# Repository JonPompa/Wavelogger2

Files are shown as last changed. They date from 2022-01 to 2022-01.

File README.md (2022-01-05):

# Wavelogger2
Underwater Pressure and Temperature logger

This project is for making a pressure / temperature logger from commercially available parts. 
The loggers run approximately 2 weeks on a battery charge and can log at a frequency of ~20Hz down to once per 30 seconds. 
THe depth limit under water is ~300m, as set by the pressure sensor. 
Data is stored on a micro SD card.

The project is inspired by Luke Miller's Open Wave Height Logger project and copies heavily from his work.
Most electrical hardware is sourced from Adafruit and the base of code is derived from their example code for the adalogger hardware.
All pressure tolerant hardware is sourced from Blue Robotics. They also provide the library for interpreting the pressure and temperature sensors.

Included files here are:
1) operating instructions for the loggers (This includes a bill of materials if anyone wants to source and build their own)
2) clock setting software for the persistent clock - direct from Adafruit
3) Operating software for the logger in its logging state
4) CAD fies for the parts tray used inside the blue robotics pressure housing
5) An assembly diagram and instructions will be developed if anyone asks for them! ( This can include a more detailed bill of materials with purchasing links)

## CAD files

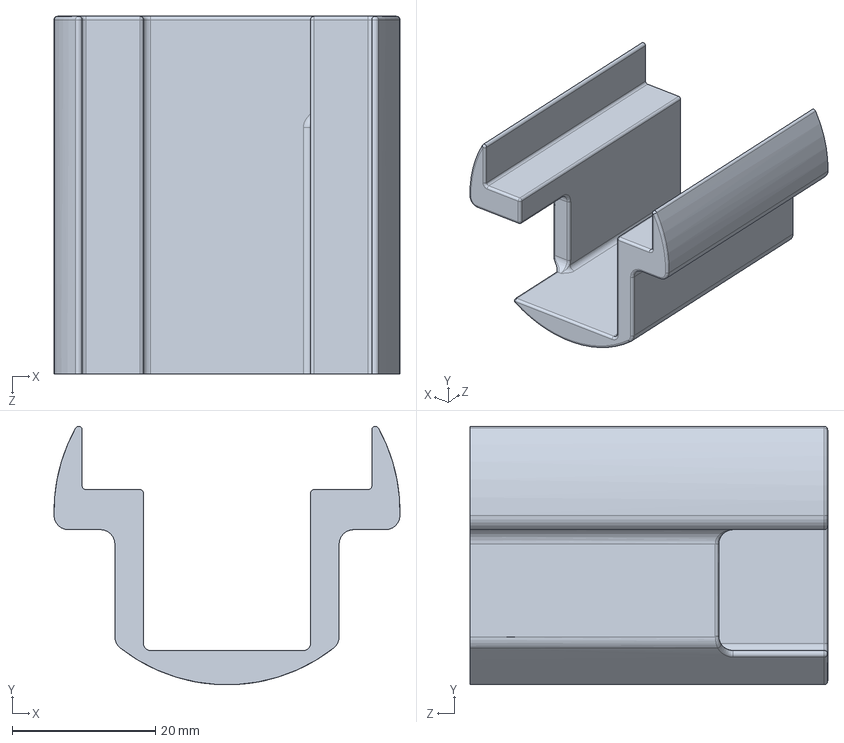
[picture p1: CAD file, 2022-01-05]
parts holder R3.SLDPRT
48.4 x 36.1 x 50.0 mm

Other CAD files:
parts holder R3.STL

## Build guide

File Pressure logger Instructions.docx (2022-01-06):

# Pressure Logger Instructions

# Overview

This pressure logger is intended for high rate, short duration pressure logging in water (ocean and fresh). Examples of typical use include wave height monitoring, coordinated tide and temperature observations, and storm surge observation.

# Specifications

Value | Range | Resolution
Depth Rating | 300m (limited by sensor)
Data Parameters
Temperature | 2-40 degrees C | 0.01 Deg C (accuracy +/- 1.5C)
Pressure | 0-30 Bar absolute | 0.2 mBar (accuracy +/- 200 mBar)
Battery Voltage | 0-5 Volts | 0.01V
Sampling Frequency | 0.5 to 20 Hz | 1 ms timing interval
Battery Capacity | 4500 mAh @ 3.7V (~14 days run time)

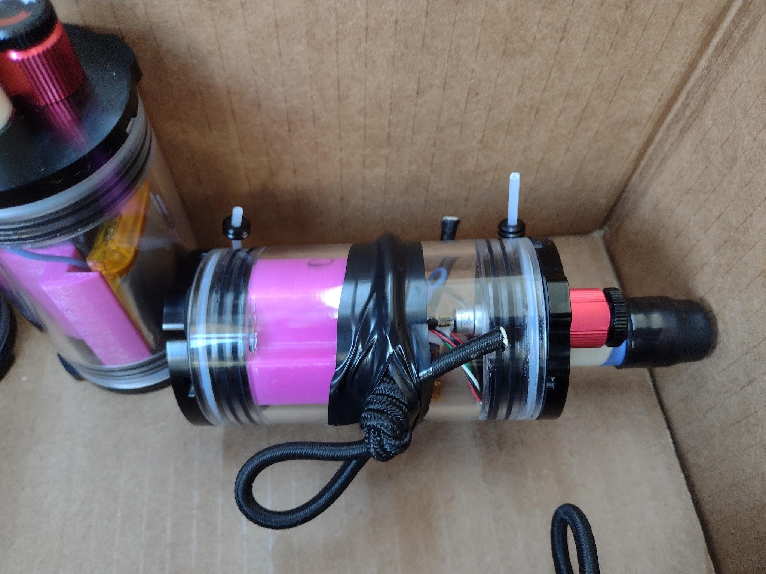
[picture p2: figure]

Pressure Logger fully assembled

# Electronics

The logger is made using an adafruit 32u4 data logger board (https://learn.adafruit.com/adafruit-feather-32u4-adalogger) and an adafruit RTC clock unit (https://learn.adafruit.com/ds3231-precision-rtc-featherwing)

The pressure sensor is from Blue Robotics (https://bluerobotics.com/store/sensors-sonars-cameras/sensors/bar30-sensor-r1 ). It includes an MS5837 absolute pressure sensor housed in a pass-through that fits into the pressure housing endcap. This sensor is rated to 300m and has a pressure resolution of 0.2 millibar. (equivalent to 2mm water depth).

Tests have shown the system maintains a noise level below 0.5 mBar in a static environment. Drift over long periods (hours) has not been well characterized yet as it needs to be compared against well-calibrated barometric pressure sensors.

The pressure sensor is not rated for continuous contact with water (readings drift), so it is protected from water by operating in a mineral-oil filled chamber. The oil is kept in the chamber by a membrane (made of a nitrile glove finger) which transmits pressure from the external water to the interior oil without influencing the pressure. This nitrile membrane is protected from damage by a rubber cap with a small hole to allow water flow.

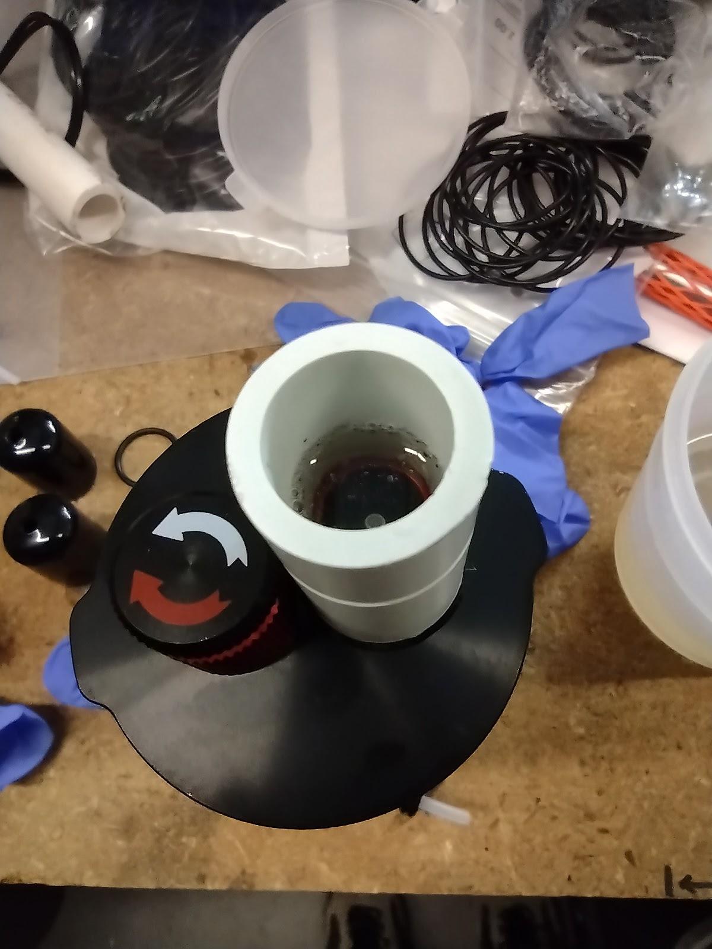
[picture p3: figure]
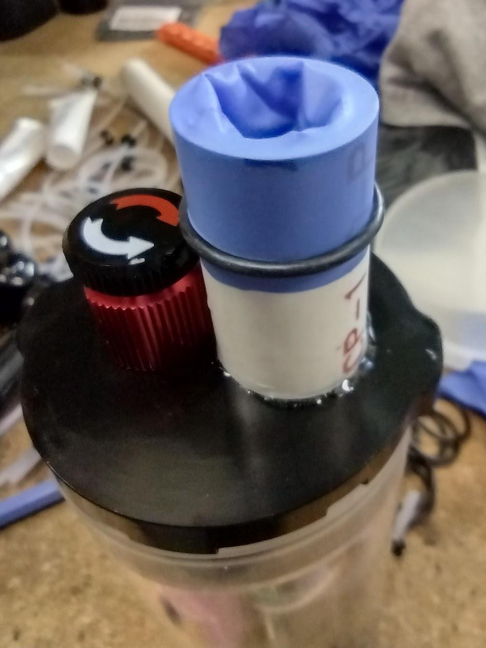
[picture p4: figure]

The pressure sensor is covered in a protective tube filled with mineral oil and covered with a nitrile membrane.

# Battery

The logger is provided with a 4500mAh battery. It is a single cell battery providing an average 3.7V with a working range from 3.2V to 4.2V. The adafruit logger board automatically turns off when the voltage reaches a minimum to avoid damaging the battery.

*NOTE ON POLARITY: The batteries provided with the loggers are wired in a “normal” direction with pin 1 of the connector negative and pin 2 positive. The Adafruit logger has a connector polarity reversed from almost all other devices that use the same connectors and battery types so it is provided with a short extension cable to reverse the polarity. When plugging in a battery, always make sure this cable is in place in the logger. When charging, always plug the battery directly into a charger without the extension cable.

There is a lithium button cell battery in the Clock board which provides constant backup power to retain the clock’s date and time reference when the main battery is removed. This is a lithium CR2012 size button cell.

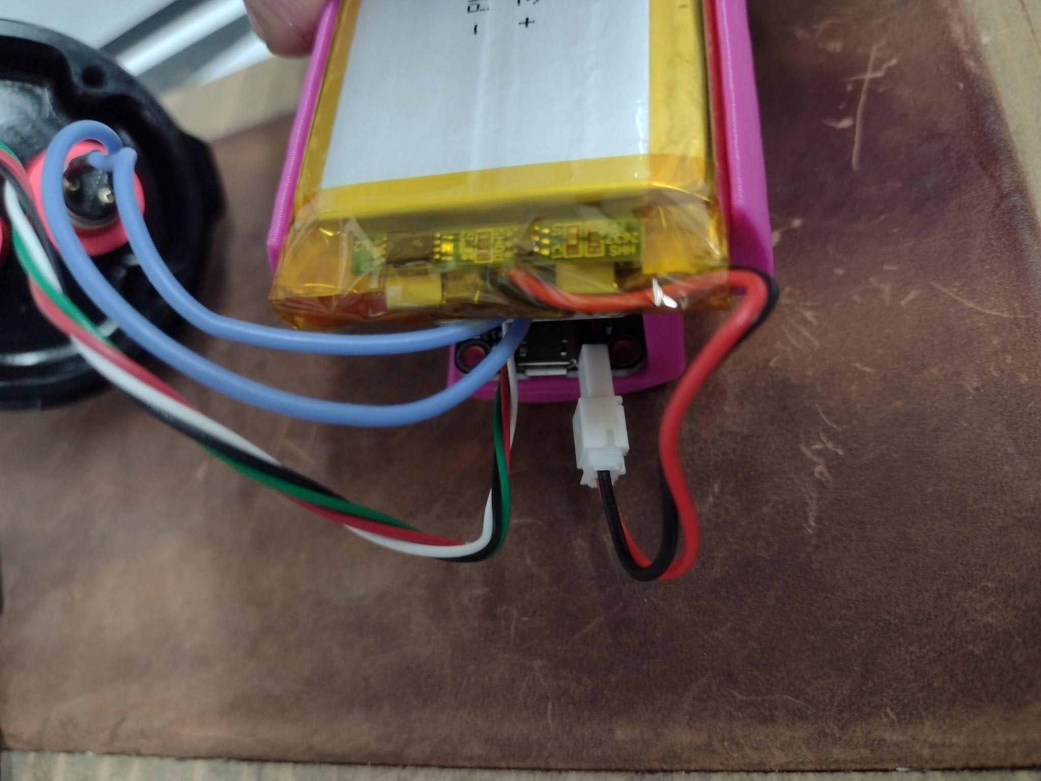
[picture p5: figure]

Battery connector: Always disconnect the battery here, not at the side of the board. The battery connector polarity is correct for the charger directly from the battery. The extension cable hidden between the circuit boards reverses the polarity for the adafruit board and should never be plugged into a charger.

# Charging

When the logger is plugged into a USB port, an internal battery charging circuit will charge the LiPo battery at a rate of 0.1A. A yellow light next to the USB port on the logger board will indicate charging is active. The light will turn off when the battery is fully charged at 4.2V. This charge rate is very low for the capacity of battery provided (4500mAh) and charging this way will take approximately 45 hours.

Using an external charger is recommended. A charger should be provided with the loggers which is capable of charging 6 batteries simultaneously at 0.6A rate.

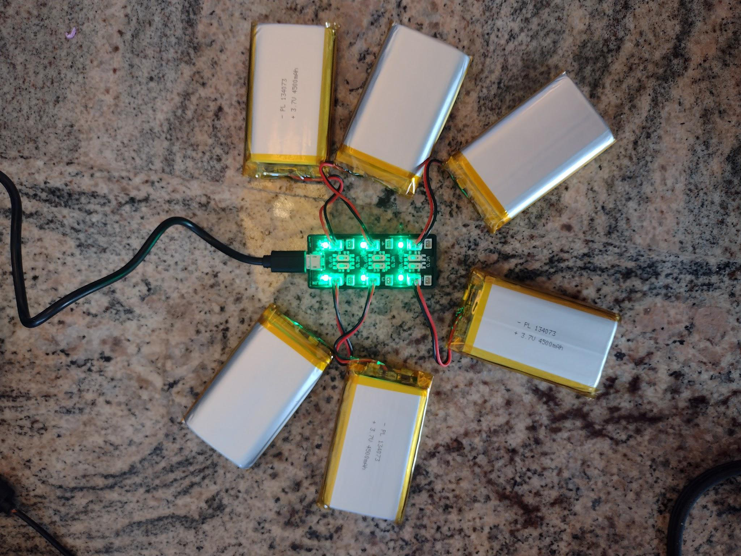
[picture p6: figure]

6 batteries attached to the external charger

# Software

Assembled loggers are pre-programmed when shipped and do not need to be programmed to record data. As of this writing, they are shipped with 4Hz sampling rate. If you prefer to change the logging parameters (such as sampling interval) you should follow the instructions below to reprogram them.

It may be helpful to reprogram the loggers occasionally to update the clock time if it has drifted or if the clock battery needs to be replaced.

The logger is programmed in the Arduino environment: Arduino IDE (download at https://www.arduino.cc/en/software)

Instructions for connecting a logger and installing are here (https://learn.adafruit.com/adafruit-feather-32u4-adalogger/setup). This gives instructions for adding the required libraries to the Arduino environment to compile this code.

The loggers should be distributed with the Arduino code sketches needed to run them,

Wavelogger2.ino and ds3231.ino, both available at https://github.com/JonPompa/Wavelogger2

The logger board has a USB port on it and can be connected with a USB cable to a computer running the Arduino IDE for programming.

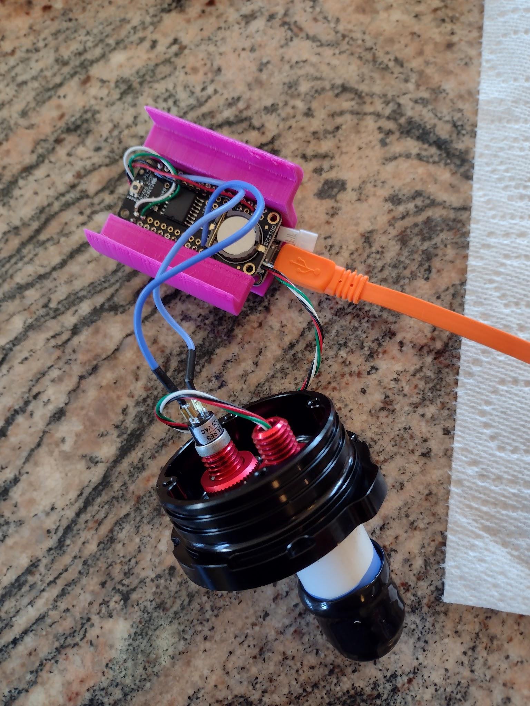
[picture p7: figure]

The logger can be connected to a computer to program it using a USB cable attached to the USB port on the logger board. This port also charges the battery (slowly) from the USB port.

Arduino sketch Ds3231.ino is used to set the RTC clock on the logger and should only need to be used once when the logger is first powered or when the button cell backup battery is replaced. DS3231.ino should be uploaded to the logger through the Arduino IDE. You can verify success by opening a serial terminal and seeing confirmation of the current time and date. (ctrl+shift+m opens a terminal window in a windows environment) The baud rate of the terminal window should be set to 56700 or whatever rate is specified in the version of ds3231.ino that you are using)

Wavelogger2 is the main program running the data collection. It should be compiled and uploaded to the logger after the ds3231.ino clock setting sketch is run. In this program, there is a set of user parameters to set for the interval between data pushes to the log file and also for frequency of sampling. The sampling interval is given in milliseconds. Know that there is also a 50ms sampling duration added to the period you specify, for example, an interval of 200ms will mean a total time between samples of 250ms, leading to a 4Hz actual sample rate.

Code example:

//User settings//

int logInterval = 4000; //milliseconds between data saves to the SD card *note max of 32000 allowed with an int data type

int senseInterval = 200; //milliseconds between data read attempts for pressure and temp sensor.

//Data reading +overhead takes about 50ms so a value of 200 here gives ~4Hz,

//Fastest achievable is about 18Hz by setting senseInterval low (5ms)

bool recordBatVolts = true; //record or don't record battery voltage

Log files are started when power is turned on. The log files are named for the date on which they start, using year, month, day format. i.e. 20210131.txt

# Assembly

The logger housing must be opened to access the data port and card reader. Once the logger has been appropriately programmed, it is not necessary to plug it into a computer to restart logging. Inserting a data card and turning on power will always initiate logging.

It is recommended to open the logger from the sensor endcap end.

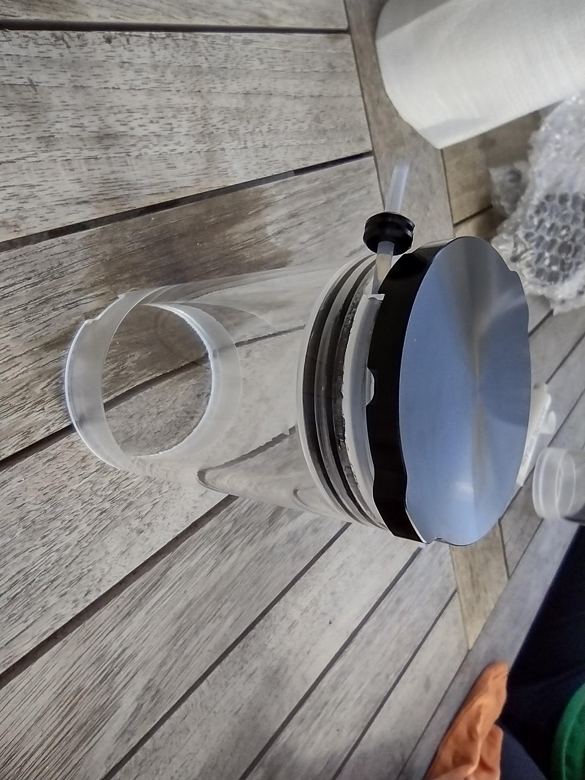
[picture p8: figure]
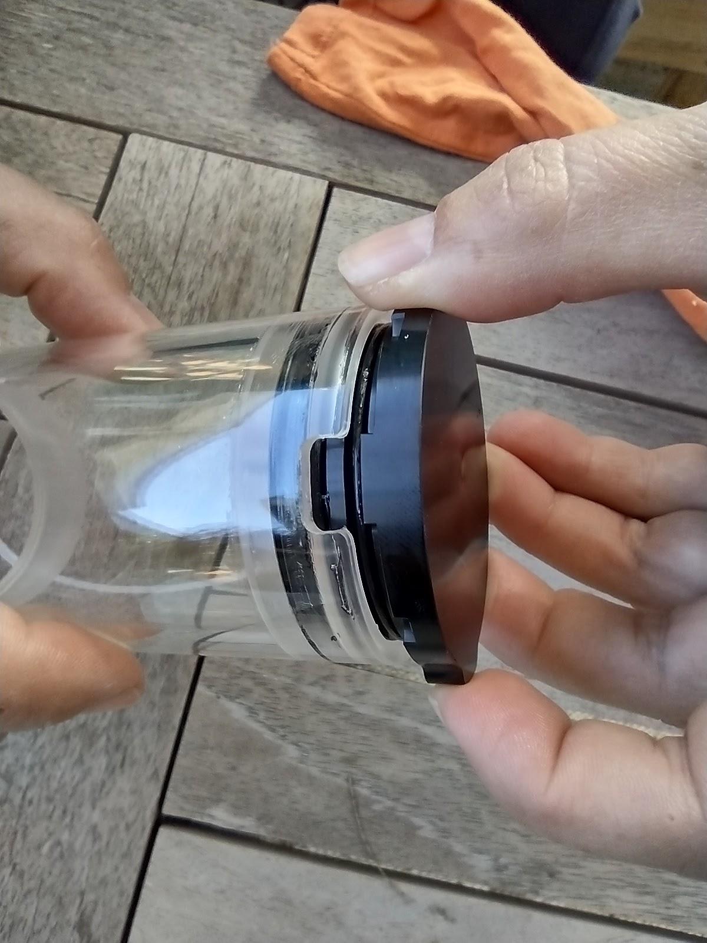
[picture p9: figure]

Opening an endcap is achieved by pulling the white plastic cord then gently sliding the endcap out by hand. Before closing an endcap, always clean and inspect orings. The orings should be lubricated with silicone grease.

To assemble the logger, slide the electronics tray (with battery) into the housing, being careful to seat the battery into the blank endcap and to align the switch and battery so that they don’t interfere. The end cap with the sensors must be rotated so that its tab aligns with the notch in the housing body for it to seat fully. See images below for important alignment notes.

The following images show some important details of how the parts fit together.

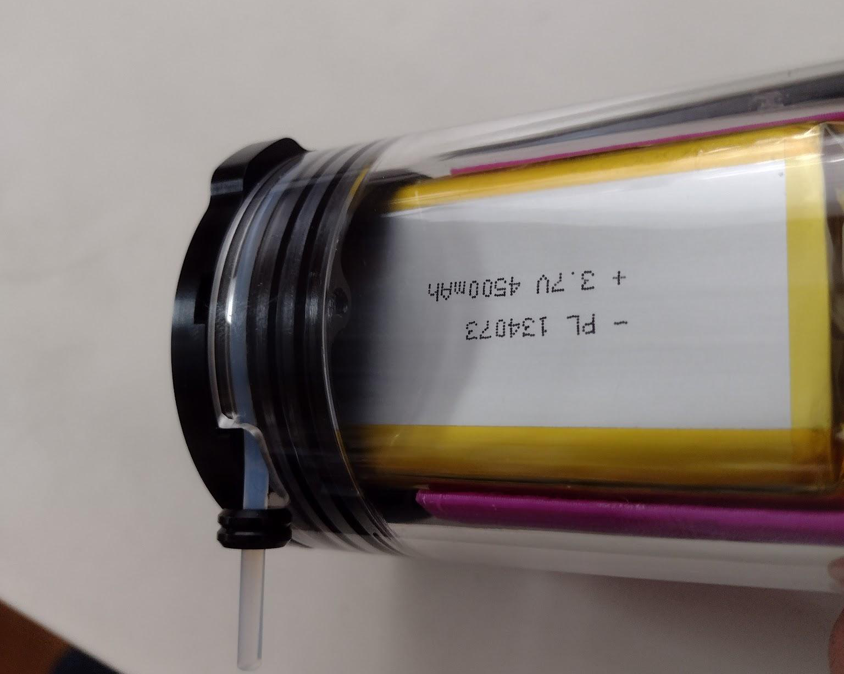
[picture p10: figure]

The battery fits down into the blank endcap when the battery and electronics tray are inserted fully into the pressure housing as shown here. This is only possible at some angles because of the shape of the endcap interior.

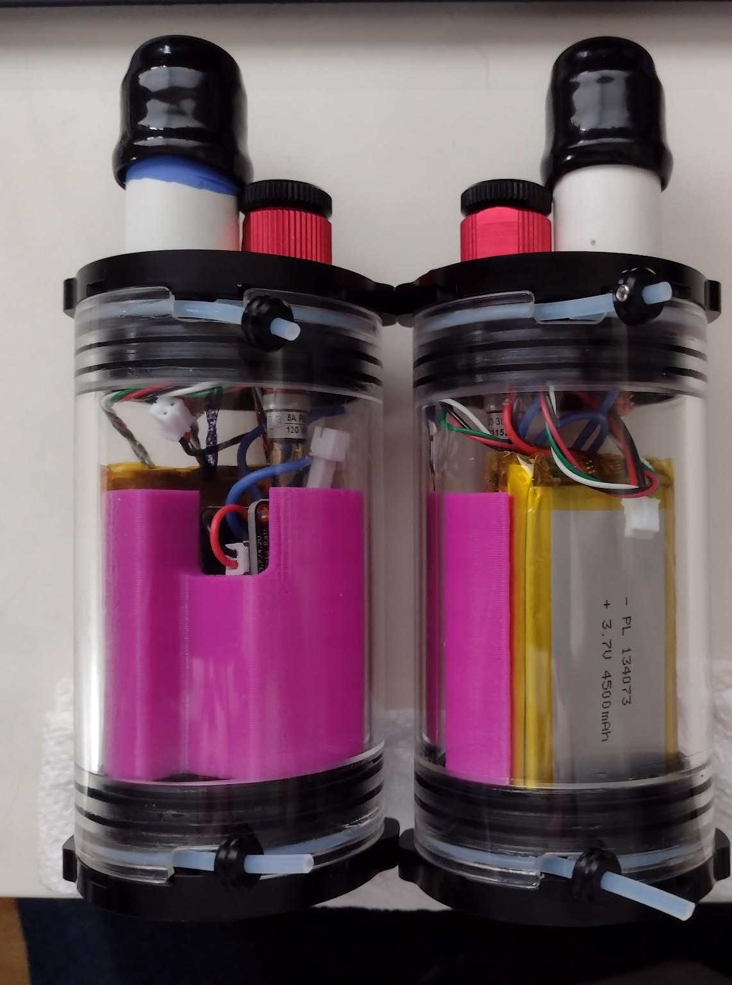
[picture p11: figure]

This image shows mirrored versions of the logger endcap. Unfortunately, some loggers were built in each configuration and the configurations require attention to assemble correctly. The notch in the housing that allows insertion of the locking cord must align with a small tab on the endcap. That alignment sets the position of the switch in the endcap. Because the switch terminals extend downward far enough to interfere with the battery, the electronics tray must be rotated to place the battery under the sensor side of the endcap, not the switch. Please pay attention to this when assembling the loggers!

The housing is sealed with o-rings on the circumference of the end caps. When the housing is assembled, the rubber o-rings must be inspected, cleaned (very carefully look for threads, fibers, and hair on the rings), and lightly greased with silicone grease.

When the end caps are pushed in, it may be helpful to remove the top of the power switch completely. This allows air to vent from the housing through a small hole (this also turns the logger on). Once the end caps are seated, they should be fastened by sliding the plastic lock cords around the circumference of the housing in the locking groove. The power switch top may then be re-inserted, being careful to note whether it is set in the on or off state. It is also helpful to inspect and grease the o-rings of the switch at this time.

# Power Switch

The logger housing can be assembled with the switch in the off position. This is when the switch top is fully screwed into the base.

At deployment time, the logger can be turned on by twisting the switch approximately one half turn in the unscrewing direction (counterclockwise).

Verify that the logger is recording by watching for an intermittent flashing of a red LED on the processor board next to the USB port. The red light flashes when data is written to the SD card, so if you have a short data writing interval, it flashes often and if you have a long data writing interval, it flashes seldom.

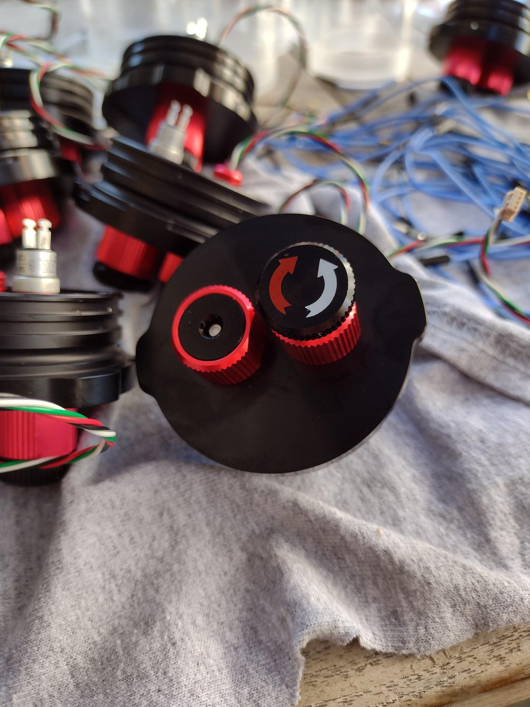
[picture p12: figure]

Here the power switch is shown on the end cap next to the bare pressure sensor. On finished loggers, the pressure sensor is protected by a cover.

# Data

Whenever the logger is turned on, it immediately starts recording data. Data is appended to an existing file if the logger has been started more than once in a day. It will start a new file if it is turned on during a new day.

Data is stored on a micro SD card which is inserted into the logger board (at the end opposite from the sensors and USB port). This card should be formatted in FAT32 format to work with the software.

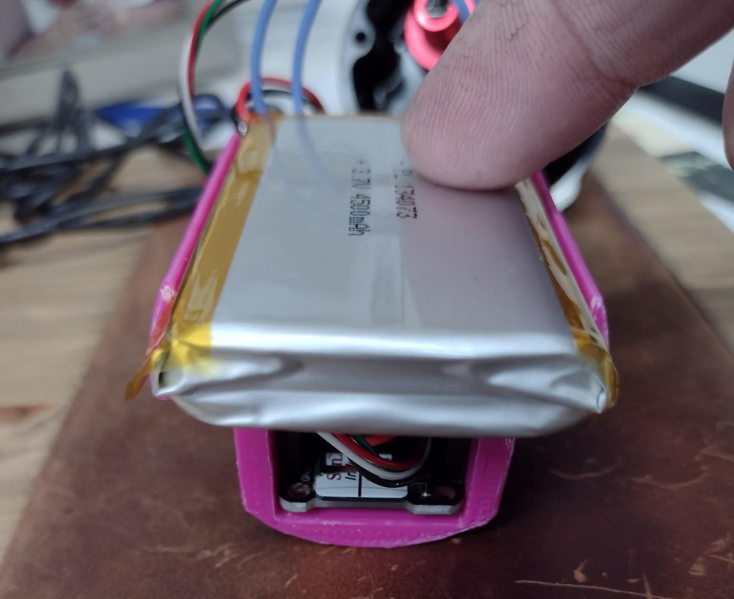
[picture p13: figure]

The SD card can be seen in its slot under the battery in this image of the disassembled logger.

Data is recorded in ASCII text format. The data fields include a header line explaining the columns. The data includes time in year, month, day, hour, min, sec, and milliseconds. The millisecond value is not referenced to the seconds value, and so may roll over independently from the count of seconds.

The data columns are:

Year Month Day Hour Minute Second Milliseconds Pressure Temperature BatteryVolts

Data for temperature is recorded in degrees C.

Data for pressure is provided in absolute millibars.

Battery voltage is recorded in volts.

*Note that as battery voltage drops for the last few hours of recording, before the low voltage cutoff shuts off the logger, the pressure reading will drift upward by several millibar.

At the time of this writing, there is no provision for retrieving data from the logger other than manually extracting the microSD card and reading it in another device. Future improvements include implementing a set of commands to retrieve the data via the USB connection and to add a USB connection through a connector on the pressure housing to prevent the need to open the loggers after each deployment.

# Data Processing

This logger records data files that become large quickly – i.e. hundreds of megabytes over a few days. Typically processing the data is best done in a scientific programming language set up for such data. Examples would be the R language, Matlab, or Python with NumPy.

A few notes on importing data follow

1) The files have a header row. This header row gives column names. If the logging was restarted within a 24 our period, there will be an extra copy of this header line in the data for each restart instance. This may challenge your data importing script!
2) The pressure data is in absolute pressure. The sensor is sensitive enough to track barometric pressure very well, so your pressure data processing may need to include an effort to obtain a local barometric pressure record and subtract that pressure from the recorded data. You may be able to use an on-shore logger to serve as a reference pressure recorder if you have a spare logger available.
3) Battery voltage is included as a debugging and convenience feature. You can reduce the data file size by turning off battery voltage logging (set the battery logging parameter value to “false” in the wavelogger2.ino file).
4) Battery voltage will influence the pressure reading when the battery is very low. Do not use the last few hours of the pressure record before the logger shuts down due to low battery state. The pressure reading will drift upward during that time.

# Mounting

The logger can be attached to a mounting location with cable ties, hose clamps, or other purpose-made clamps around the housing body. If using hose clamps, you may want to cover the clamp in a rubber tube such as a bicycle tire inner tube to prevent scratching the housing. If using cable-ties, it is suggested to avoid nylon cable ties which lose a significant amount of their strength when submerged in water over time.

# Credits

This manual is a living document and is subject to change.

This logger has been designed by Jon Pompa using readily available parts and code as referenced above.

Major inspiration was taken from Luke Miller’s Open Wave Height Logger project (which provides a much higher level of documentation, testing, and a longer-duration logger design)

Much of this project is also built on the Adalogger family of devices from Adafruit which provide nearly complete hardware and software out of the box.

The underwater housings and sensors are stock items from Blue Robotics.

# Contact

Please direct questions or ideas to Jon Pompa - jon@reefgen.io

Plans for incremental upgrades at the moment include data access and battery charging by connector, better wire management, and mounting brackets.

If anyone wants a construction manual for building these loggers, please make a request.

# Bill of Materials

Part | | Qty
Pressure housing
| Blue robotics 2" x 100mm housing | 1
| Blue robotics 2" blank endcap with flange | 1
| Blue robotics 2" endcap 2 hole with flange | 1
| BR switch / vent penetrator (modified to vent) | 1
| BR Bar30 pressure sensor | 1
| BR sealing cord (included with endcaps) | 2
| BR sealing orings (included with endcaps) | 4
Electronics
| Adafruit Adalogger 32u4 | 1
| Adafruit precision RTC featherwing | 1
| SD card | 1
| stacking header pins | 2
| header pins (included with adalogger) | 1
| Lipo single cell 4500mAh 13x40x72mm | 1
| CR1220 button cell (3V lithium) | 1
| Mounting bracket (parts holder_R2.sldprt) | 1
Sensor protection
| PVC 1/2 pipe bored out for sensor plus oring groove | 1
| 5min epoxy (gorilla) to seal pvc to sensor | 1
| Nitrile glove finger | 1
| mineral oil | 1
| Rubber cap (with hole) to go over pvc pipe | 1
| oring m2x17.5 | 1

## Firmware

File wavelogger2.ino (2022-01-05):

//Pressure and temperature logger to run on an adafruit adalogger 32u4 with precision RTC featherwing board
//Set your sampling frequency using "senseInterval" variable. Log writing frequency is independent of sampling frequency and can be set by logInterval
//battery voltage logging can be turned on or off
//To set the rtc, use sketch "ds3231" in the RTC examples

#include <MS5837.h>
#include <Wire.h>
#include <RTClib.h>
#include <SD.h>
#define VBATPIN A9 
MS5837 sensor;
RTC_DS3231 rtc;

//User settings//
int logInterval = 4000; //milliseconds between data saves to the SD card *note max of 32000 allowed with an int data type
int senseInterval = 200; //milliseconds between data read attempts for pressure and temp sensor. 
                        //Data reading +overhead takes about 50ms so a value of 200 here gives ~4Hz,
                        //Fastest achievable is about 18Hz by setting senseInterval low (5ms)
bool recordBatVolts = true; //record or don't record battery voltage


unsigned long lastSenseMils = 0;
unsigned long lastLogMils = 0;
File logFile;
int led = 13;

void setup() {
  Serial.begin(57600);
  //add a light so we can see the file write is happening

  pinMode(led, OUTPUT); 
  Serial.println("Starting");
  if (! rtc.begin()) {
    Serial.println("Couldn't find RTC");
    abort();
  } 

  delay(2000);
  openLogFile();
  
  Wire.begin();
  // Initialize pressure sensor
  // Returns true if initialization was successful
  // We can't continue with the rest of the program unless we can initialize the sensor
  while (!sensor.init()) {
    Serial.println("Pressure sensor init failed!");
    delay(1000);
  }
  // .init sets the sensor model for us but we can override it if required.
  // Uncomment the next line to force the sensor model to the MS5837_30BA.
  sensor.setModel(MS5837::MS5837_30BA);
  sensor.setFluidDensity(1029); // kg/m^3 (freshwater, 1029 for seawater)

}

void loop() {
  // put your main code here, to run repeatedly:
  if( (millis()-lastSenseMils) > senseInterval){
    doSensing();
    lastSenseMils = millis();
  }
  if( (millis()-lastLogMils) > logInterval){
    digitalWrite(led, HIGH);   // turn the LED on (HIGH is the voltage level)
    logFile.flush();
    lastLogMils = millis();
    digitalWrite(led, LOW);   // turn the LED on (HIGH is the voltage level)
  }
  //delay(10);
}

void doSensing() {
  // Update pressure and temperature readings
  sensor.read();
  
  /* //Serial debug
  Serial.print("Pressure: ");
  Serial.print(sensor.pressure());
  Serial.println(" mbar");

  Serial.print("Temperature: ");
  Serial.print(sensor.temperature());
  Serial.println(" deg C");

  Serial.print("Depth: ");
  Serial.print(sensor.depth(),4);
  Serial.println(" m");

  Serial.println(millis()%1000);
  */
  
  DateTime now = rtc.now(); 
  logFile.print(now.year(), DEC);logFile.print(' ');
  logFile.print(now.month(), DEC);logFile.print(' ');
  logFile.print(now.day(), DEC);logFile.print(' ');
  logFile.print(now.hour(), DEC);logFile.print(' ');
  logFile.print(now.minute(), DEC);logFile.print(' ');
  logFile.print(now.second(), DEC);logFile.print(' ');
  logFile.print(millis()%1000);logFile.print(" ");
  
  logFile.print(sensor.pressure());logFile.print(" ");
  logFile.print(sensor.temperature());logFile.print(" ");

  if(recordBatVolts){
    float measuredvbat = analogRead(VBATPIN);
    measuredvbat *= 2;    // we divided by 2, so multiply back
    measuredvbat *= 3.3;  // Multiply by 3.3V, our reference voltage
    measuredvbat /= 1024; // convert to voltage
    logFile.println(measuredvbat);
    //Serial.print("VBat: " ); Serial.println(measuredvbat);
  } else{           
     logFile.println(" ");
  }
}


void openLogFile(){
  Serial.print("Initializing SD card...");
  pinMode(4, OUTPUT);
 
  if (!SD.begin(4)) {
    Serial.println("initialization failed!");
    return;
  }
  Serial.println("SD initialization done.");
  
  DateTime now = rtc.now();
  char timeStamp[24] = "YYYYMMDD.txt";
  logFile = SD.open(now.toString(timeStamp), FILE_WRITE);
  //logFile = SD.open(timeStamp, FILE_WRITE);
  if(logFile){
    Serial.println("opened logFile");
    //logFile.println("new start");
    logFile.println("YYYY MM DD hh mm ss millisecs Pressure(mB) Temp(C) BatteryVolts");    
  } else {
    // if the file didn't open, print an error:
    Serial.println("error opening log file");
  }
  //logfile.close; 
  return logFile; 
}
